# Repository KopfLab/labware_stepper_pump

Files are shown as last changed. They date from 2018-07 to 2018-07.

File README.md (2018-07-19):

# labware_stepper_pump

## wiring diagram

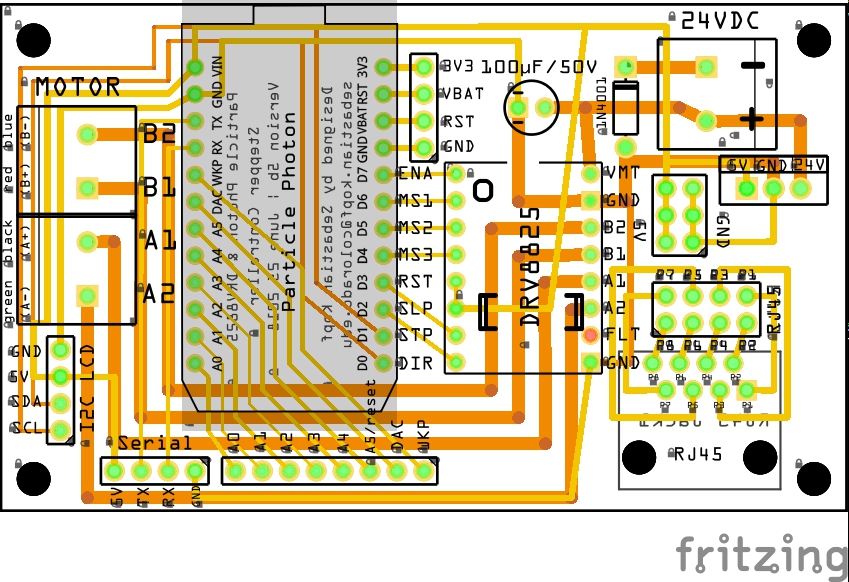
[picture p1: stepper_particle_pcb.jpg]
Stepper Photon PCB
 

## stepper setup: adjusting driver current limit

 - it is crucial to adjust the current limit properly to always be < the rated current/phase of the stepper motor (if too high then can damage the motor and driver, if too low won't get full torque and get the annoying scretching). The full step mode will only use 70% of this max current the driver allows but all microstepping modes will energize up to the set current limit.
 - there is a good standard tutorial on how to adjust this available here (the youtube video is extremely helpful): https://www.pololu.com/product/2133
 - in theory for the DRV8825, the reference voltage measured between logic ground and the trim pot (Vref) x 2 = resulting current limit (so e.g. for limiting current to 1A, ref in theory should be set to 0.5V)
 - in practice, however, this can vary quite a bit (maybe quality of resistors on DRV8825 board? or maybe the ref. voltage supplied by the particle photons), and it is highly advisable to actually check the current per phase once the trim pot is set (and then adjust as needed)
 - this is done most easily by adjusting the trim pot (power to the board but not running the stepper!) to the theoretical 1/2 of the max rated current/phase of the stepper, then putting the multimeter in series with one of the coils of the stepper and starting the stepper at a very low speed so you can easily watch it step the current through this coil up and down and figure out the maximum current it is running at
 - for example, for a stepper online stepper (Nema 17 planetary geared stepper) with 1.8 step angle and 5.18 gear ratio, max current per phase of 1.68A the following Vrefs resulted in the following max currents in full step and microstepping modes:
  - 406mV --> 370mA in full step,  620mA in microstepping
  - 564mV --> 540mA in full step,  860mA in microstepping
  - 696mV --> 660mA in full step, 1070mA in microstepping
  - 893mV --> 860mA in full step, 1390mA in microstepping
  - This is actually an almost perfect linearity of 1.6 instead of 2
 - NOTE: the trim pot voltage is most easily adjusted with a voltmeter attached to the screwdriver (easer with flat head than with cross)

### Watson Marlow stepper motor pump head

  - adjust to <= 1200mA in microstepping mode (Vref ~ 700mV - 800mV), make sure to check the current as described above

## particle photon setup

 - setup the [Particle Photon](https://store.particle.io/collections/photon) microcontroller (via Wifi and cell phone or via computer and command line interface), instructions in the [Particle Docs](https://docs.particle.io/guide/getting-started/start/photon/)
 - clone this repository to preferred location on your local harddrive
 - easiest use of this repository:
  - install the [Particle Interactive Development Environment](https://www.particle.io/products/development-tools/particle-desktop-ide)
  - load the cloned repository folder in the  Particle IDE
  - adjust the parameters in `pump.ino` that define the used pins and characteristics of the stepper (e.g. steps, etc.)
  - login into your particle account in the Particle IDE
  - select the Photon flash the code (lightning bolt symbol) over WIFI
  - that's it, if wired correctly you should now have full access to your pump's functionality from your local command line anywhere via the particle cloud
 - alternatively, use [build.particle.io](http://build.particle.io)
  - log in to the Particle web interface and create a new project
  - add the `AccelStepper` (and if used the `LiquidCrsytal_I2C`) libraries to your project from the online library tab
  - add the remaining `.h` and `.cpp` files in the repository to your project and upload the `.ino` file's content to the main project file
  - select the target Particle Photon and flash the program

## web commands

To run these web commands, you need to either have the [Particle Cloud command line interface (CLI)](https://github.com/spark/particle-cli) installed, or format the appropriate POST request to the [Particle Cloud API](https://docs.particle.io/reference/api/). Here only the currently implemented CLI calls are listed but they translate directly into the corresponding API requests (see `pump_control.html` file for an example implementation via javascript).

#### access via POST

Download and open the `pump_control.html` file and fill in your particle account's access token and the device name or ID. You only have access to the photons that are registered to your account.

#### requesting information via CLI

The state of the pump can be requested by calling `particle get <deviceID> state` where `<deviceID>` is the name of the photon you want to get state information from. The return value is an array string (ready to be JSON parsed) that includes information on status, speed, direction, microstepping, locked/unlocked, etc. Make sure to be logged in (`particle login`) to have access to your photons.

#### issuing commands via CLI

All calls are issued from the terminal and start with `particle call <deviceID>` where `<deviceID>` is the name of the photon you want to issue a command to. If the command was successfully received and executed `0` is returned, if the command was received but cause and error, a negative number (e.g. `-1` for generic error, `-2` for unknown command, etc.) is the return value. Positive return values mean executed with warning (e.g. `1` for generic warning, `2` means had to set to max rpm instead of requested). You can change all of the following command's exact wording and all the return codes in `PumpCommands.h` if you want them to be different. Make sure to be logged in (`particle login`) to have access to your photons.

  - `particle call pump "start"` to start the pump (at the currently set speed and microstepping)
  - `... pump "stop"` to stop the pump and disengage it (no holding torque applied)
  - `... pump "hold"` to stop the pump but hold the position (maximum holding torque)
  - `... pump "rotate <x>"` to have the pump do `<x>` rotations and then execute a `stop` commands
  - `... pump "ms <x>"` to set the microstepping mode to `<x>` (1= full step, 2 = half step, 4 = quarter step, etc.)
  - `... pump "ms auto"` to set the microstepping mode to automatic in which case the lowest step mode that the current speed allows will be automatically set
  - `... pump "speed <x> rpm"` to set the pump speed to `<x>` rotations per minute (if the pump is currently running, it will change the speed to this and keep running). if microstepping mode is in `auto` it will automatically select the appropriate microstepping mode for the selected speed. If the microstepping mode is fixed and the requested rpm exceeds the maximally possible speed for the selected mode (or if in `auto` mode, the requested rpm exceeds the fastest possible on full step mode), the maximum speed will automatically be set instead and a warning return code will be issued.
  - `... pump "direction cc"` to set the direction to counter clockwise
  - `... pump "direction cw"` to set the direction to clockwise
  - `... pump "direction switch"` to reverse the direction (note that any direction changes stops the pump if it is in `rotate <x>` mode)
  - `... pump "lock"` to lock the pump (i.e. no commands will be accepted until `unlock` is called)
  - `... pump "unlock"` to unlock the pump if it is locked
  - to be continued (more commands in progress)...

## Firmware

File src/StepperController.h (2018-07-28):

#pragma once
#include "StepperState.h"
#include "StepperConfig.h"
#include "StepperCommands.h"
#include "device/DeviceController.h"
#include <AccelStepper.h>

// stepper controller class
class StepperController : public DeviceController {

  private:

    // internal functions
    void construct();
    void updateStepper(bool init = false); // update stepper object
    float calculateSpeed(); // calculate speed based on settings
    int findMicrostepIndexForRpm(float rpm); // finds the correct ms index for the requested rpm (takes ms_auto into consideration)
    bool setSpeedWithSteppingLimit(float rpm); // sets state->speed and returns true if request set, false if had to set to limit

    // configuration
    StepperBoard* board;
    StepperDriver* driver;
    StepperMotor* motor;
    AccelStepper stepper;

    // state
    StepperState* state;
    DeviceState* ds = state;

    // startup
    bool startup_rpm_logged = false;

  public:

    // constructors
    StepperController() {};

    StepperController (int reset_pin, DeviceDisplay* lcd, StepperBoard* board, StepperDriver* driver, StepperMotor* motor, StepperState* state) :
      DeviceController(reset_pin, lcd), board(board), driver(driver), motor(motor), state(state) {
        construct();
    };

    // methods
    void init(); // to be run during setup()
    void update(); // to be run during loop()

    float getMaxRpm(); // returns the maximum rpm for the pump

    bool changeDataLogging (bool on);
    bool changeStatus(int status);
    bool changeDirection(int direction);
    bool changeSpeedRpm(float rpm); // return false if had to limit speed, true if taking speed directly
    bool changeToAutoMicrosteppingMode(); // set to automatic microstepping mode
    bool changeMicrosteppingMode(int ms_mode); // set microstepping by mode, return false if can't find requested mode

    bool start(); // start the pump
    bool stop(); // stop the pump
    bool hold(); // hold position
    long rotate(float number); // returns the number of steps the motor will take

    DeviceState* getDS() { return(ds); }; // return device state
    void saveDS(); // save device state to EEPROM
    bool restoreDS(); // load device state from EEPROM

    void clearData(bool all) ;
    bool assembleDataLog();
    void logRpm();

    void assembleStateInformation();
    void updateStateInformation();

    void parseCommand();
    bool parseStatus();
    bool parseDirection();
    bool parseSpeed();
    bool parseMS();

};

/**** SETUP AND LOOP ****/

void StepperController::construct() {
  driver->calculateRpmLimits(board->max_speed, motor->steps, motor->gearing);
  data.resize(2);
  // same index to allow for step transition logging
  data[0] = DeviceData(1, "speed", "rpm", 1);
  data[0].setAutoClear(false); // not cleared during auto clear
  data[1] = DeviceData(1, "speed", "rpm", 1);
}

void StepperController::init() {

  DeviceController::init();

  stepper = AccelStepper(AccelStepper::DRIVER, board->step, board->dir);
  stepper.setEnablePin(board->enable);
  stepper.setPinsInverted	(
            driver->dir_cw != LOW,
            driver->step_on != HIGH,
            driver->enable_on != LOW
        );
  stepper.disableOutputs();
  stepper.setMaxSpeed(board->max_speed);

  // microstepping
  state->ms_index = findMicrostepIndexForRpm(state->rpm);
  state->ms_mode = driver->getMode(state->ms_index);
  pinMode(board->ms1, OUTPUT);
  pinMode(board->ms2, OUTPUT);
  pinMode(board->ms3, OUTPUT);
  #ifdef STEPPER_DEBUG_ON
    Serial.println("INFO: available microstepping modes");
    for (int i = 0; i < driver->ms_modes_n; i++) {
      Serial.printf("   Mode %d: %s steps, max rpm: %.1f\n", i, driver->ms_modes[i].mode, driver->ms_modes[i].rpm_limit);
    }
  #endif

  updateStepper(true);
}

// loop function
void StepperController::update() {
  if (state->status == STATUS_ROTATE) {
    // WARNING: FIXME known bug, when power out, saved rotate status will lead to immediate stop of pump
    if (stepper.distanceToGo() == 0) {
      changeStatus(STATUS_OFF); // disengage if reached target location
      updateStateInformation();
    } else {
      stepper.runSpeedToPosition();
    }
  } else {
    stepper.runSpeed();
  }

  // log rpm once startup is complete
  if (startup_logged && !startup_rpm_logged) {
    logRpm();
    startup_rpm_logged = true;
  }

  DeviceController::update();
}

/**** STATE PERSISTENCE ****/

// save device state to EEPROM
void StepperController::saveDS() {
  EEPROM.put(STATE_ADDRESS, *state);
  #ifdef STATE_DEBUG_ON
    Serial.println("INFO: stepper state saved in memory (if any updates were necessary)");
  #endif
}

// load device state from EEPROM
bool StepperController::restoreDS(){
  StepperState saved_state;
  EEPROM.get(STATE_ADDRESS, saved_state);
  bool recoverable = saved_state.version == STATE_VERSION;
  if(recoverable) {
    EEPROM.get(STATE_ADDRESS, *state);
    Serial.printf("INFO: successfully restored state from memory (version %d)\n", STATE_VERSION);
  } else {
    Serial.printf("INFO: could not restore state from memory (found version %d), sticking with initial default\n", saved_state.version);
    saveDS();
  }
  return(recoverable);
}

/**** UPDATING STEPPER ****/

void StepperController::updateStepper(bool init) {
  // update microstepping
  if (state->ms_index >= 0 && state->ms_index < driver->ms_modes_n) {
    digitalWrite(board->ms1, driver->ms_modes[state->ms_index].ms1);
    digitalWrite(board->ms2, driver->ms_modes[state->ms_index].ms2);
    digitalWrite(board->ms3, driver->ms_modes[state->ms_index].ms3);
  }

  // update speed
  stepper.setSpeed(calculateSpeed());

  // update enabled / disabled
  if (state->status == STATUS_ON || state->status == STATUS_ROTATE) {
    stepper.enableOutputs();
  } else if (state->status == STATUS_HOLD) {
    stepper.setSpeed(0);
    stepper.enableOutputs();
  } else {
    // STATUS_OFF
    stepper.setSpeed(0);
    stepper.disableOutputs();
  }

  // log rpm (if necessary - determined in function)
  if (!init) logRpm();
}

float StepperController::calculateSpeed() {
  float speed = state->rpm/60.0 * motor->steps * motor->gearing * state->ms_mode * state->direction;
  #ifdef STEPPER_DEBUG_ON
    Serial.printf("INFO: calculated speed %.5f\n", speed);
  #endif
  return(speed);
}

/* DEVICE STATE CHANGE FUNCTIONS */

bool StepperController::changeDataLogging (bool on) {
  bool changed = DeviceController::changeDataLogging (on);
  if (on && changed) logRpm();
  return(changed);
}

bool StepperController::changeStatus(int status) {

  // only update if necessary
  bool changed = status != state->status;

  #ifdef STEPPER_DEBUG_ON
    if (changed)
      Serial.printf("INFO: status updating to %d\n", status);
    else
      Serial.printf("INFO: status unchanged (%d)\n", status);
  #endif

  if (changed) {
    state->status = status;
    updateStepper();
    saveDS();
  }
  return(changed);
}

bool StepperController::changeDirection(int direction) {

  // only update if necessary
  bool changed = (direction == DIR_CW || direction == DIR_CC) && state->direction != direction;

  #ifdef STEPPER_DEBUG_ON
    if (changed)
      (direction == DIR_CW) ? Serial.println("INFO: changing direction to clockwise") : Serial.println("INFO: changing direction to counter clockwise");
    else
      (direction == DIR_CW) ? Serial.println("INFO: direction unchanged (clockwise)") : Serial.println("INFO: direction unchanged (counter clockwise)");
  #endif

  if (changed) {
    state->direction = direction;
    if (state->status == STATUS_ROTATE) {
      // if rotating to a specific position, changing direction turns the pump off
      #ifdef STEPPER_DEBUG_ON
        Serial.println("INFO: stepper stopped due to change in direction during 'rotate'");
      #endif
      state->status = STATUS_OFF;
    }
    updateStepper();
    saveDS();
  }

  return(changed);
}

bool StepperController::changeSpeedRpm(float rpm) {
  int original_ms_mode = state->ms_mode;
  float original_rpm = state->rpm;
  state->ms_index = findMicrostepIndexForRpm(rpm);
  state->ms_mode = driver->getMode(state->ms_index); // tracked for convenience
  setSpeedWithSteppingLimit(rpm);
  bool changed = state->ms_mode != original_ms_mode | fabs(state->rpm - original_rpm) > 0.0001;

  #ifdef STEPPER_DEBUG_ON
    if (changed)
      Serial.printf("INFO: changing rpm %.3f\n", state->rpm);
    else
      Serial.printf("INFO: rpm staying unchanged ()%.3f)\n", state->rpm);
  #endif

  if (changed) {
    updateStepper();
    saveDS();
  }
  return(changed);
}

bool StepperController::setSpeedWithSteppingLimit(float rpm) {
  if (driver->testRpmLimit(state->ms_index, rpm)) {
    state->rpm = driver->getRpmLimit(state->ms_index);
    Serial.printf("WARNING: stepping mode is not fast enough for the requested rpm: %.3f --> switching to MS mode rpm limit of %.3f\n", rpm, state->rpm);
    return(false);
  } else {
    state->rpm = rpm;
    return(true);
  }
}

bool StepperController::changeToAutoMicrosteppingMode() {

  bool changed = !state->ms_auto;

  #ifdef STEPPER_DEBUG_ON
    if (changed)
      Serial.println("INFO: activating automatic microstepping");
    else
      Serial.println("INFO: automatic microstepping already active");
  #endif

  if (changed) {
    state->ms_auto = true;
    state->ms_index = findMicrostepIndexForRpm(state->rpm);
    state->ms_mode = driver->getMode(state->ms_index); // tracked for convenience
    updateStepper();
    saveDS();
  }
  return(changed);
}

bool StepperController::changeMicrosteppingMode(int ms_mode) {

  // find index for requested microstepping mode
  int ms_index = driver->findMicrostepIndexForMode(ms_mode);

  // no index found for requested mode
  if (ms_index == -1) {
    Serial.printf("WARNING: could not find microstep index for mode %d\n", ms_mode);
    return(false);
  }

  bool changed = state->ms_auto | (state->ms_index != ms_index);
  #ifdef STEPPER_DEBUG_ON
    if (changed)
      Serial.printf("INFO: activating microstepping index %d for mode %d\n", ms_index, ms_mode);
    else
      Serial.printf("INFO: microstepping mode already active (%d)\n", state->ms_mode);
  #endif

  if (changed) {
    // update with new microstepping mode
    state->ms_auto = false; // deactivate auto microstepping
    state->ms_index = ms_index; // set the found index
    state->ms_mode = driver->getMode(ms_index); // tracked for convenience
    setSpeedWithSteppingLimit(state->rpm); // update speed (if necessary)
    updateStepper();
    saveDS();
  }
  return(changed);
}

int StepperController::findMicrostepIndexForRpm(float rpm) {
  if (state->ms_auto) {
    // automatic mode --> find lowest MS mode that can handle these rpm (otherwise go to full step -> ms_index = 0)
    return(driver->findMicrostepIndexForRpm(rpm));
  } else {
    return(state->ms_index);
  }
}

// start, stop, hold
bool StepperController::start() { return(changeStatus(STATUS_ON)); }
bool StepperController::stop() { return(changeStatus(STATUS_OFF)); }
bool StepperController::hold() { return(changeStatus(STATUS_HOLD)); }

// number of rotations
long StepperController::rotate(float number) {
  long steps = state->direction * number * motor->steps * motor->gearing * state->ms_mode;
  stepper.setCurrentPosition(0);
  stepper.moveTo(steps);
  changeStatus(STATUS_ROTATE);
  return(steps);
}

/***** DATA INFORMATION *****/

void StepperController::clearData(bool all) {
  // never clear persistent data
  DeviceController::clearData(false);
}

bool StepperController::assembleDataLog() {
  // always reset time offset to 0
  data[0].setNewestDataTime(millis());
  data[0].saveNewestValue(false); // no averaging
  // individual time offsets
  return(DeviceController::assembleDataLog(false));
}
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

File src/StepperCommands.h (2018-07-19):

// status
#define CMD_START       "start" // device start [msg] : starts the stepper
#define CMD_STOP        "stop" // device stop [msg] : stops the stepper (stops power)
#define CMD_HOLD        "hold" // device hold [msg] : engage the stepper but not running (power on, no flow)
#define CMD_RUN         "run" // device run minutes [msg] : runs the stepper for x minutes
#define CMD_AUTO        "auto" // device auto [msg] : listens to external trigger on the trigger pin
#define CMD_ROTATE      "rotate" // device rotate number [msg] : run for x number of rotations

// direction
#define CMD_DIR         "direction" // device direction cw/cc/switch [msg] : set the direction
  #define CMD_DIR_CW      "cw"
  #define CMD_DIR_CC      "cc"
  #define CMD_DIR_SWITCH  "switch"

// speed
#define CMD_SPEED       "speed" // device speed number rpm/fpm [msg] : set the stepper speed
  #define SPEED_RPM       "rpm" // device speed number rpm [msg] : set speed in rotations per minute (requires step-angle)
#define CMD_RAMP        "ramp"  // device ramp number rpm/fpm minutes [msg] : ramp speed from current to [number] rpm/fpm over [minutes] of time

// microstepping
#define CMD_STEP        "ms" // device ms number/auto [msg] : set the microstepping
  #define CMD_STEP_AUTO   "auto" // signal to put microstepping into automatic mode (i.e. always pick the highest microstepping that the clockspeed supports)

// warnings
#define CMD_RET_WARN_MAX_RPM      101
#define CMD_RET_WARN_MAX_RPM_TEXT "exceeds max rpm"

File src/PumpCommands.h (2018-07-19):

// PUMP SPECIFIC COMMANDS - NOT IMPLEMENTED YET FIXME
#define CMD_DISPENSE    "dispense" // pump dispense amount [msg] : dispense a certain amount (requires step-flow calibration)

#define CMD_SET         "calibrate" // pump calibrate variable value [msg]
#define SET_STEP_FLOW   "step-flow" // set flow per step (step-flow)
#define SET_ROT_FLOW    "rotation-flow" // set step-flow (step-flow) from flow per rotation [requires step-angle]
#define SET_FPM         "fpm" // set step-flow (step-flow) from flow per minute [requires step-angle and current speed]

#define SPEED_FPM       "fpm" // pump speed number fpm [msg] : set speed in flow per minute (requires step-flow calibration)

#define CMD_RET_ERR_SET  -4
#define ERROR_SET        "unknown calibrate"

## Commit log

2017-02-19 pump control classes v0.1
2017-02-19 pump sketch first draft
2017-02-21 pump commands clarification for step-angle (no longer used)
2017-03-11 driver current adjustment guide
2017-03-11 EEPROM pump state storage implemented
2017-03-11 use system thread to improve stepper timing
    [stepper_motor.fzz]
2017-03-11 max speed increased to 1000 step/s (enabled by asynchronous system threading)
2017-03-12 pump settings in separate file
2017-03-12 pump state information introduced
2017-03-12 expose pump state to spark api
2017-03-12 pump control web interface first draft
2017-03-18 pump pcb for particle photon / DRV8825 driven stepper
    [pump_pcb.fzz, pump_pcb_contour.gm1, pump_pcb_copperBottom.gbl, pump_pcb_copperTop.gtl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]
2017-04-06 pump control to include manual mode
2017-05-16 update pump control w/ command history and timeout controller
2018-07-12 initial update (not functional)
    [stepper_motor_wiring.fzz]
2018-07-15 update stepper controller, state and config
2018-07-15 basic compiling stepper controller
2018-07-16 cleanup pcb and stepper code
    [pump_pcb.fzz, pump_pcb_contour.gm1, pump_pcb_copperBottom.gbl, pump_pcb_copperTop.gtl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]
2019-07-04 update device template
